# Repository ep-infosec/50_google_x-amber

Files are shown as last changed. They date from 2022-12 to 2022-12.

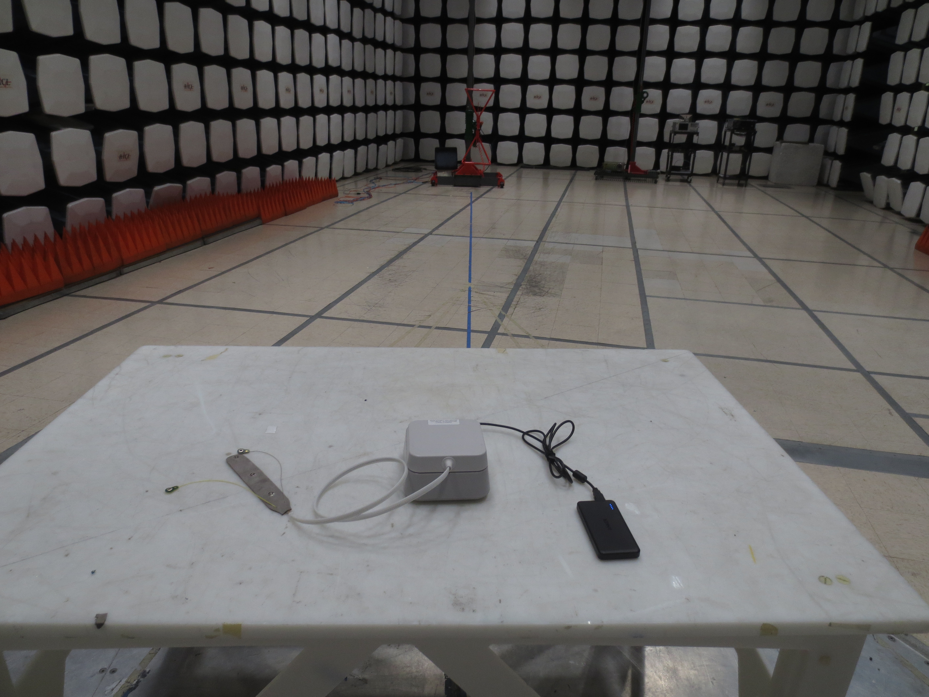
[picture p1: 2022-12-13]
hardware/test/safety reports/IMG_0185.JPG

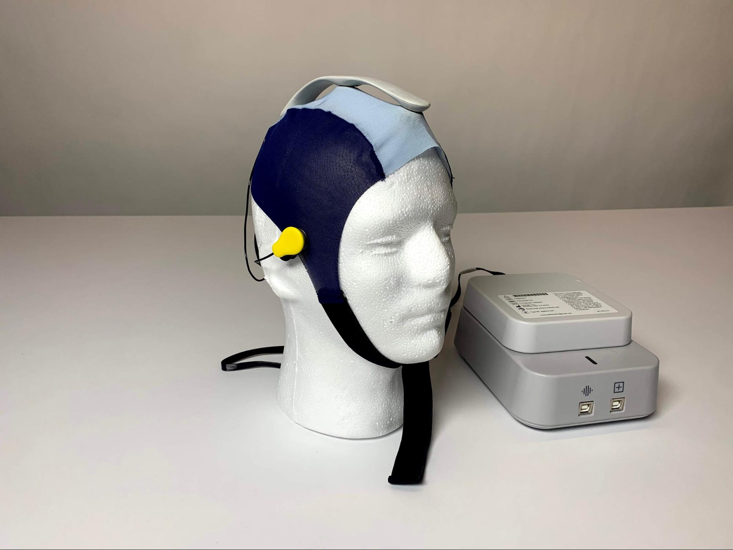
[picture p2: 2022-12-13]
hardware/overview/system_photo.jpg

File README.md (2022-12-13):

# NOTICE
* The materials covered by the associated license relate to a general purpose product and its underlying designs, schematics, and hardware and software code (collectively “Contributions”), none of which have been evaluated, cleared or approved for any medical or other purpose by and may not meet applicable safety or other legal or regulatory requirements of any governmental agency, including but not limited to the United States Food and Drug Administration (“FDA”), or equivalent regulatory bodies outside of the US.
* Any use of the term “EEG” or “electroencephalogram” contained in the Contribution is for informational purposes only and does not label, represent or otherwise indicate the Contribution is intended to be used or has been reviewed or approved as a medical device by the US FDA or equivalent regulatory bodies outside of the US.
* Any article, material or other publication by any person or entity referencing the use or operation of the Contribution for a medical or other any other purpose is for informational purposes only; does not directly or indirectly represent or infer any intended use in the diagnosis of disease or other conditions, or in the cure, mitigation, treatment, or prevention of disease, in people or animals; and does not label, represent or otherwise indicate the Contribution is intended to be used or has been reviewed or approved as a medical device by the US FDA or equivalent regulatory bodies outside of the US.
* While the Contributions may have potential medical applications, many countries, including the US, require regulatory approvals prior to using any device in the diagnosis of disease or other conditions, or in the cure, mitigation, treatment, or prevention of disease, in people or animals.
* It is the user’s responsibility to secure all necessary regulatory approvals and meeting all applicable government safety and environmental standards associated with use of the Contributions.

# Components
This codebase consists of the following components:
* **Software** components below are under Apache 2.0 License:
  1. **Stimulus software** is under `stimulus/` directory.
  2. **Collect software** is under `collect/` directory.
  3. **Firmware** is under `firmware/` directory.
  4. **Flash Tool** is under `flash_tool/` directory.
* **Hardware design** is under CC BY 4.0 License and located in `hardware/` directory.

Please refer to the `README` file and documentations in each respective
directory for more details.

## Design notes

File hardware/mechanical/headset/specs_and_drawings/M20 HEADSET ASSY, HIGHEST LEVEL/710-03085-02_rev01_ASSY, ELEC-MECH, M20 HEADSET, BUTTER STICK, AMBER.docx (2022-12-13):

ITEM ⁴ ³ ² ¹

NUMBER DESCRIPTION MANUFACTURER MFG PART NUMBER QTY.

REVISIONS

1 710-03081-01 ASSY, ELECT-MECH, M20 ADAPTER, BUTTER STICK, AMBER N/A N/A 1

ECO REV. DESCRIPTION BY DATE

2 725-01312-01 ASSY, HARNESS, CABLE, LINEAR SENSORESTRIP N/A N/A 1

ECO-033387 01 INITIAL RELEASE EMT 12/19/2019

3 961-00021-01 LABEL, 5 SENSOR HEADSET, AMBER N/A N/A 1

D

D3 1 2 CCB BCENTER LABEL HORIZONTALLY & FROM APPROXIMATELY BOTTOM EDGE, 11mm AS SHOWN

TEXT ORIENTATION

CONFIDENTIAL THIS DOCUMENT AND THE DATA DISCLOSED HEREIN OR DRAWN

DATE WHEREWITH IS NOT TO BE REPRODUCED, USED, OR RD/EMT/DSF 1/3/2020 A11 DISCLOSED IN WHOLE OR IN PART TO ANYONE WITHOUT THE PERMISSION OF GOOGLE, INC.

CHECKED

DATE G. LEVINE 1/3/2020

43 SHEET 1 OF 1

100 Mayfield Avenue Mountain View CA 94043 UNLESS OTHERWISE SPECIFIED ENGINEER DIMENSIONS ARE IN MILLIMETERS

USA

A

TOLERANCES UNLESS OTHERWISE NOTED:

1.

FOR ASSEMBLY: REFER TO MPI-0306-00, ASSEMBLY INSTRUCTIONS. X X.X X.XX ANGLES

1.0 0.3 .1 .25

G. LEVINE 1/3/2020

THIRD ANGLE

MATERIAL

N/A

TITLE

ASSY, ELEC-MECH, M20 HEADSET, BUTTER STICK, AMBER

2.

PART REQUIRES PACKAGING TO PREVENT DAMAGE DURING SHIPMENT. PROJECTION

FINISH

1.6

N/A

SIZE BSURFACE ROUGHNESS

UNLESS OTHERWISE SPECIFIED

BREAK SHARP EDGES TO <0.4 MM

DO NOT SCALE DRAWING

1:10 710-03085-02 2 1

PART NUMBER

710-03085-02

REV

01

INTERPRET DRAWING PER ASME Y14.5-2009

SCALE

FILE NAME

MASS (g):

267.64

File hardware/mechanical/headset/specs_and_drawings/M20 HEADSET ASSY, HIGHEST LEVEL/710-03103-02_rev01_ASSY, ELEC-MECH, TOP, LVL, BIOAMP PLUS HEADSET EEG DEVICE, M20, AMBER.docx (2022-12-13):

ITEM ⁴ ³ ² ¹

NUMBER DESCRIPTION MANUFACTURER MFG PART NUMBER QTY.

1 710-03064-01 ASSY, M20 BIOAMP, BUTTER DISH, AMBER N/A N/A 1

2 710-03085-02 ASSY, ELEC-MECH, M20 HEADSET, BUTTER STICK, AMBER N/A N/A 1

D DCC1 2 B BACONFIDENTIAL

THIS DOCUMENT AND THE DATA DISCLOSED HEREIN OR DRAWN RD/EMT/DSF WHEREWITH IS NOT TO BE REPRODUCED, USED, OR DISCLOSED IN WHOLE OR IN PART TO ANYONE WITHOUT THE PERMISSION OF GOOGLE, INC.

CHECKED

G. LEVINE DATE

1/3/2020 DATE

1/3/2020 100 Mayfield Avenue Mountain View CA 94043 UNLESS OTHERWISE SPECIFIED ENGINEER DIMENSIONS ARE IN MILLIMETERS

USA

A

TOLERANCES UNLESS OTHERWISE NOTED:

G. LEVINE 1/3/2020 MATERIAL

TITLE 1. PART REQUIRES PACKAGING TO PREVENT DAMAGE DURING SHIPMENT. 2.

PART PACKAGING REQUIRES LABELING OF PART NUMBER AND MANUFACTURER NAME X X.X X.XX ANGLES

SIZE BDO NOT SCALE DRAWING N/A

710-03103-02 688.65 43 2 1

SHEET 1 OF 1 1.0 0.3 1. .25

THIRD ANGLE

N/A

ASSY, ELEC-MECH, TOP, LVL, BIOAMP PLUS HEADSET EEG DEVICE, M20, AMBER

PROJECTION

FINISH

1.6

N/A

SURFACE ROUGHNESS

UNLESS OTHERWISE SPECIFIED

PART NUMBER 710-03103-02

REV

01

SCALE

FILE NAME

MASS (g):

BREAK SHARP EDGES TO <0.4 MM

INTERPRET DRAWING PER ASME Y14.5-2009

REVISIONS

ECO REV. DESCRIPTION BY DATE

ECO-033387 01 INITIAL RELEASE EMT 12/19/2019

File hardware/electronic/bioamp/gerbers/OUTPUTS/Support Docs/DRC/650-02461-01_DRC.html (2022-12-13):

Altium

# Design Rule Verification Report

Date: | | 5/15/2019
Time: | | 4:19:37 PM
Elapsed Time: | | 00:00:04
Filename: | | G:\My Drive\Amber\6. Hardware\Bio-amplifier Schematics and PCB Files\Luchador Rev 3.2b\Pcb\Luchador Pcb.PcbDoc

Warnings: | | 0
Rule Violations: | | 5

## Summary

Warnings | Count
Total | 0

Rule Violations | Count
Clearance Constraint (Gap=6mil) (All),(All) | 5
Clearance Constraint (Gap=10mil) (InNamedPolygon('PWR GND') Or InNamedPolygon('BOT GND') Or InNamedPolygon('SL2 GND') Or InNamedPolygon('SL1 GND') Or InNamedPolygon('TOP GND')),(All) | 0
Clearance Constraint (Gap=10mil) (InNamedPolygon('-2.5V')),(All) | 0
Short-Circuit Constraint (Allowed=No) (All),(All) | 0
Un-Routed Net Constraint ( (All) ) | 0
Modified Polygon (Allow modified: No), (Allow shelved: No) | 0
Width Constraint (Min=6mil) (Max=100mil) (Preferred=10mil) (All) | 0
Power Plane Connect Rule(Direct Connect )(Expansion=20mil) (Conductor Width=10mil) (Air Gap=10mil) (Entries=4) (All) | 0
Hole To Hole Clearance (Gap=10mil) (All),(All) | 0
Net Antennae (Tolerance=0mil) (All) | 0
Height Constraint (Min=0mil) (Max=1000mil) (Prefered=500mil) (All) | 0
Total | 5

Clearance Constraint (Gap=6mil) (All),(All)

Clearance Constraint: (Collision < 6mil) Between Arc (3056mil,4335mil) on Keep-Out Layer And Pad J8-M(3056mil,4335mil) on Multi-Layer

Clearance Constraint: (Collision < 6mil) Between Arc (3056mil,4460mil) on Keep-Out Layer And Pad J8-M(3056mil,4460mil) on Multi-Layer

Clearance Constraint: (201617.964mil < 6mil) Between Arc (3156mil,4335mil) on Keep-Out Layer And Pad J8-M(3156mil,4335mil) on Multi-Layer

Clearance Constraint: (Collision < 6mil) Between Arc (3256mil,4335mil) on Keep-Out Layer And Pad J8-M(3256mil,4335mil) on Multi-Layer

Clearance Constraint: (Collision < 6mil) Between Arc (3256mil,4460mil) on Keep-Out Layer And Pad J8-M(3256mil,4460mil) on Multi-Layer

Back to top

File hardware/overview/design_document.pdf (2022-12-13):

# Draft: 2019-08 AMBER M20 EEG Acquisition System Design Document

### 1. The M20 Bioamplifier

M20 is a 32 channel EEG acquisition system. It is designed to be connected to a PC USB port for data communication.

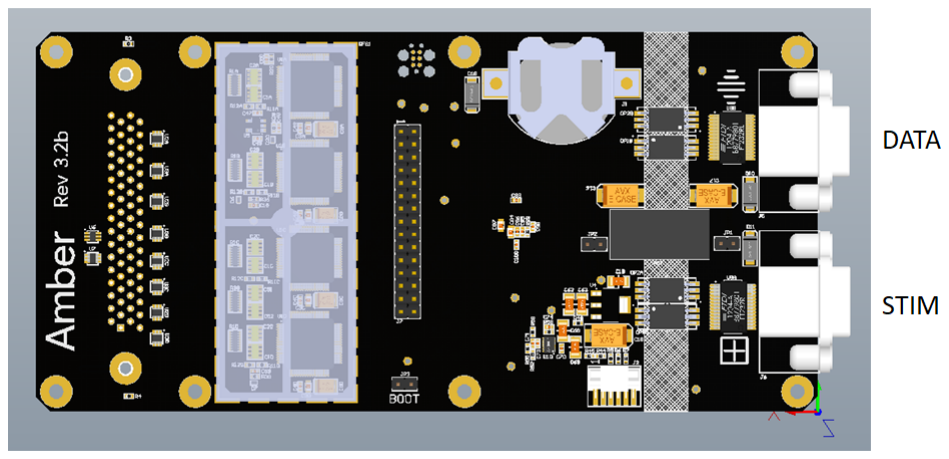
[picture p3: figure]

### 1. Hardware Design

### 1.1. DAQ

The heart of the design is the ADS1299 8 channel bioamplifier from Texas Instruments. This single IC provides the front-end amplification and 24 bit conversion. It is particularly suitable for EEG measurements as it provides a ground bias generator and built-in lead-off detection.

4 of the ADS1299s are connected together in a parallel data configuration. All 4 together provide 32 EEG channels. U1A is the master ADS1299 and provides the conversion clock to the other 3 converters to keep things synchronized. U1A is also the master bias generator.

Although the ADS1299 can provide differential or single-ended inputs, the configuration of the board allows for only single-ended inputs on channels 1-24, and the option of single-ended or differential inputs on channels 25-32.

The sample rate is 250 samples per second.

Communication with the MCU is over 4 wire SPI running at a clock speed of 4 MHz. The ADS1299 provides a signal (#DRDY) that goes low when a conversion is ready to be read out of the chip. Only the master has this signal connected to the MCU and as all timing is referenced to it. Individual chip selects are asserted to read the data from each of the ADS1299s in turn. An alternate option would be to read the data in a daisy-chain configuration, but the parallel configuration was chosen for its speed and flexibility.

### 1.2. MCU

The MCU is a Kinetis (NXP/Freescale) KL27Z256 in a 64 pin QFP package. This is an Arm Cortex M0 processor running at 48 MHz with 256K of flash memory. The reasons for choosing this processor include the speed, cost, availability, and ease of development with the Kinetis tool chain.

Debugging is done through a dedicated JTAG port implemented with a special TAG connect cable. Production programming is done through the DATA USB port utilizing the built-in ROM bootloader and a special Python tool.

The MCU handles the data conversion from the ADS1299s and communication with the host PC. It is also responsible for monitoring the on-board power supplies.

4 input pins allow for identifying the hardware revision through pull-down resistors. 4 pins are also reserved for future expansion.

Although the MCU has low-power modes, in this design it is always running at full power.

### 1.3. Power Supplies

Power to the board comes from either one of the 2 USB connectors. USB voltage is diode-ORed and powers an isolated DC/DC converter (PS1). This provides the 4kv isolation and patient leakage current protection. Jumpers JP1 and JP2 must be installed for normal operation. These were implemented to provide power flexibility in the event a battery would need to be used.

The 5V output of the DC/DC converter is linear regulated down to 3.3V. A linear regulated was chosen to provide a lower noise floor than another DC/DC. The 3.3V primary powers the MCU and digital logic.

A charge pump based converter also runs off the 3.3V rail and provides the +/-2.5V rails to the ADS1299s. Normally charge pumps are rather noisy, but this particular IC (LM27762) has built-in linear regulators following the charge pumps and is tailored to these sorts of applications.

A separate 2.5V reference is also generated to power the MCU analog section and to provide a precise reference for power supply measurements.

### 1.4. USB Ports

Two USB ports connect the PCB to a PC. The DATA port is used to transfer the streaming EEG data. The STIM port allows control of the board and is used to set marks in the EEG data stream.

Each port uses an FTDI232 USB to serial IC on the PC side. The MCU side implements optical isolators for patient protection. These are rated at 4kv with a maximum data rate of 10Mbps.

### 1.5. Real Time Clock

A real time clock is implemented. It communicates over I2C with the MCU and has battery backup.

### 1.6. Micro SD

A micro SD slot is provided for future expansion. It is connected to a second SPI port on the MCU.

### 1.7. Expansion/Debug Header

Board test and expansion signals are brought to this header. They are labeled in the layout and provide an easy means of testing or debugging the board.

### 2. Layout

The PCB is designed as a 6 layer board. The layer stack is signal, ground plane, signal, signal, power connections, signal. Minimum line/space is 6/6 and minimum via size is 6/16. Board material is plain FR4 and finish is ENIG. This is standard for today’s fabrication processes and allows the board to be manufactured at any number of board houses.

The board is separated into 3 distinct sections: PC non-isolated, digital, and analog.

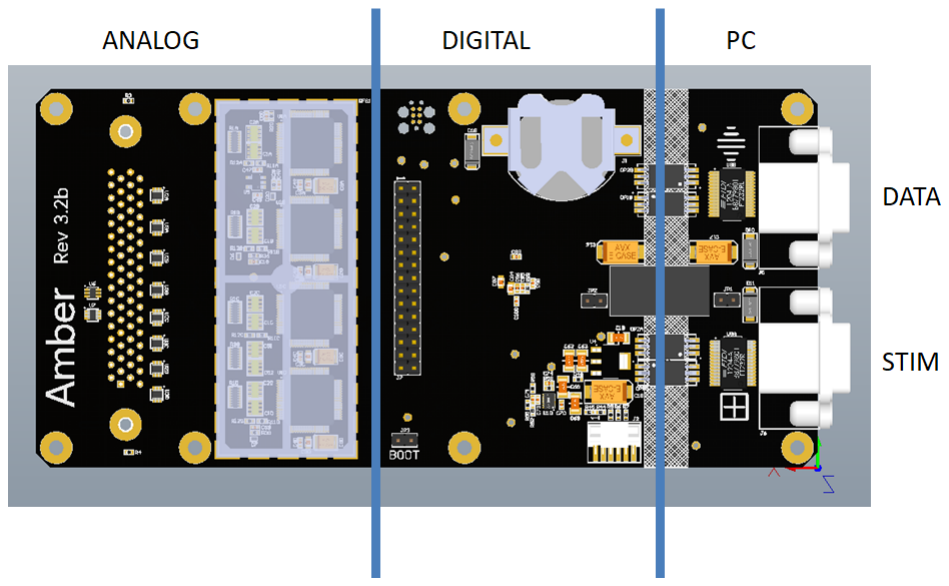
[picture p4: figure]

### 2.1. PC

The PC side has the USB ports and half the optical isolators and DC/DC converter. Creepage and clearance is maintained at 8mm.

### 2.2. Digital

The digital section incorporates the power supplies and MCU. The expansion header is also included here.

### 2.3. Analog

The analog section protects the microvolt level EEG signals from the noisy digital sections. An RF shield is included that encapsulates the ADS1299 converters. A split ground plane separates the sensitive ground returns from the noisy digital grounds:

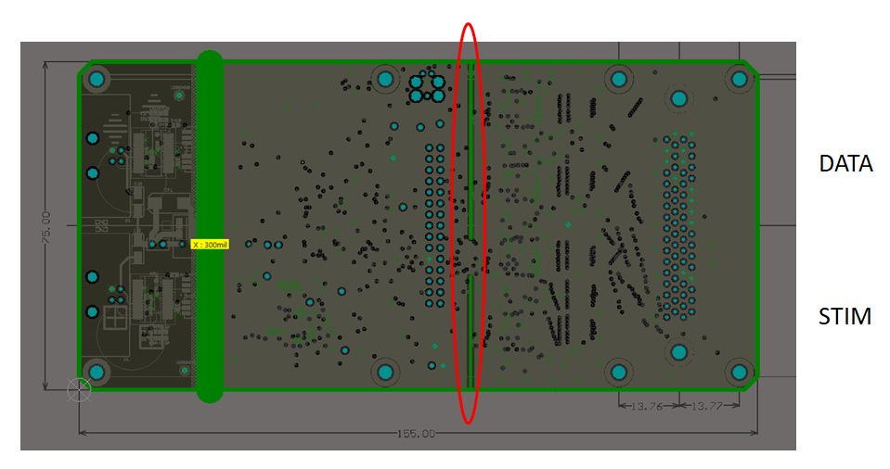
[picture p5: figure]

### 2.4. Test Points

Various individual test points are provided as well as the debug header for future automated testing.

### 3. Firmware

The firmware was developed in C using the Kinetis Design Studio. Some functions were developed with the help of Kinetis’s Processor Expert which simplifies MCU configuration parameters. Some low-level drivers were hand written for the high performance and low latency needed processing the EEG data.

A main loop handles gathering EEG data, doing serial communication, and blinking LEDs. Some tasks are event driven such as EEG data ready and serial communication. These typically either buffer the data or raise flags for processing in the main loop.

A text based command line interpreter (CLI) is implemented for easy control and communication. Any terminal program can be used for sending commands. Although the CLI will respond to commands from either port, only characters on the STIM port are echoed. CLI responses on the DATA port are multiplexed with the streaming EEG data by prefixing ‘CLI:’ to the response line. Commands to the CLI are terminated by a carriage return.

EEG data is continuously streamed on the DATA port in ASCII format. Each channel is comma separated and the EEG value is encoded as a signed 24 bit value. A frame of EEG data has the following format:

SEQUENCE NUMBER | CH 1 | CH 2 | … | CH32 | MARK | CR/LF

The frame is prefixed by ‘DATA:’. The sequence number is an auto incrementing unsigned 32 bit value. The mark is a user-selected data value appended to the EEG stream. Each line is terminated by a carriage return/line feed.

M20 Active Sensor Breakout Board Design Document

## 1. Overview

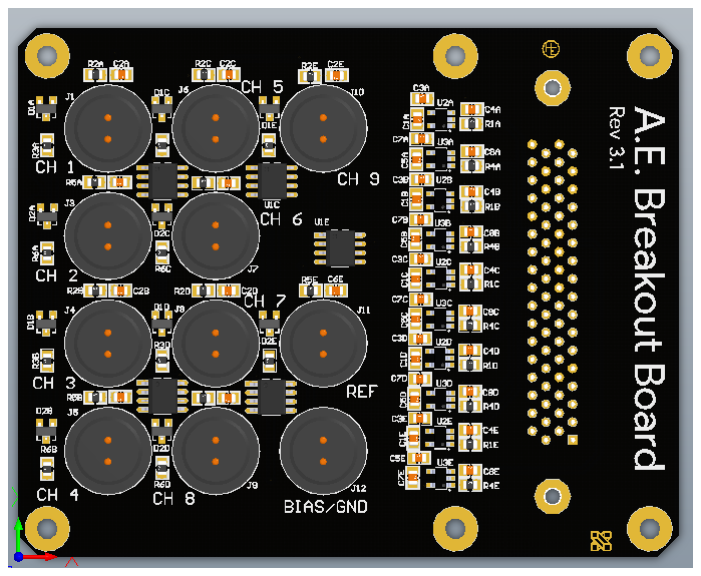
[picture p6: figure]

Conventional wet EEG sensors rely on electrolytic gels to penetrate hair and provide a clean conductive path between sensor and skin. The gel also 'fills-in' potential gaps formed between the sensor and skin during application and subject movement. The use of wet EEG sensors is time consuming and uncomfortable for the subject.

The M20 bioamplifier program remedies this by using dry electrodes. Dry electrodes have a higher impedance than wet electrodes. M20’s dry electrode solution combines sensors with mechanics and electronics which match the higher impedance. These are known as active sensors. A high impedance preamplifier circuit is integrated with the dry sensor to provide the bioamp with a clean signal. Typical active sensors require three wires, 2 for power and 1 for the signal. M20’s active sensors are powered by a current source requiring only 2 wires running to the electrode. The circuitry for the current source is integrated into the active electrodes adapter board that plugs into the bioamp.

The Active Electrode Breakout Board is used with the AMBER EEG Bioamplifer to make electrical connections with the test subject. It includes 9 channels of EEG plus reference and bias connections.

## 2. Design

## 2.1. Electrical

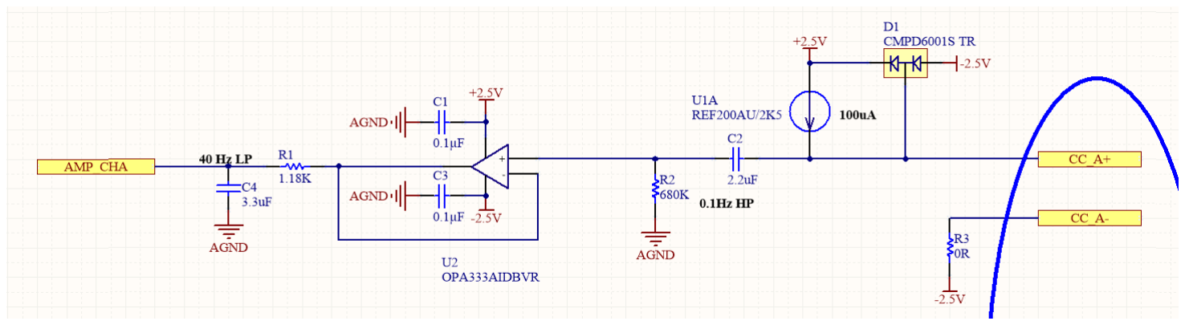
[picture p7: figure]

The electrical design of each EEG channels includes a 100uA current source. This powers the electrode, which is an operation-amplifier operating in a bootstrap mode. Microvolt signals from the operational amplifier electrode are high-pass filtered at 0.1Hz and buffered, then low-pass filtered at 40 Hz. This filtered and buffered signal is presented to the bioamplifier board.

The reference electrode is similarly processed as an EEG electrode.

The bias electrode is simply passed through without any electrical processing.

## 2.2. Mechanical

## 2.2.1. Electrodes

The electrodes connect to the breakout board through an industry-standard touchless connector from Plastics1. The touchless connector ensures that no electrical conductor can be accidently touched during the operation of the EEG system.

## 2.2.2. Main Connector

The connection to the AMBER bioamplifier is made through a 68 pin vertical SCSCI connector.

## 2.2.3. PCB

The PCB is a 4 layer standard FR-4 substrate. The size is 94x75mm.

Firmware Design

## 1. Overview

The firmware for the Amber project is responsible for taking EEG samples from the ADS1299 and formatting them for serial delivery to an external PC. It will also accept commands from a second serial port that is running a basic CLI (Command Line Interpreter). It is designed to run on an NXP MKL27Z256VLH4 processor.

## 2. Structure

All of the code runs in a single thread; therefore, each task must maintain its own state machine and relinquish orderly control to prevent the system from blocking. Each task is called from the main loop in the main.c module. The tasks are as follows:

1. Leds
2. EEG
3. Serial

## 2.1. Processor Expert

Processor Expert is an automatic code and configuration generator by NXP. It is used to speed up development of firmware for specific microcontrollers by abstracting to driver-level code. It is used extensively in this project. The modules will be described later in this document.

## 3. Modules

## 3.1. main.c

The entry point into the firmware is main.c. However, before the first line in main.c has been executed, C initialization routines have already been run to initialize static data structures. This occurs in the background and is invisible to the developer.

The first task is to initialize the Processor Expert(PE) modules. This includes setting the CPU clock and operating modes.

Following the PE initialization, the firmware initializes serial communication, LEDs, SPI communication (used with the ADS1299 converters), and EEG data structures. After initialization is complete, the main loop starts to service the LED, EEG, and serial tasks.

## 3.2. eeg.c

This module is responsible for high-level communication with the ADS1299. It includes functions for initializing the converters and reading and writing the ADS1299 registers. The EEG task checks if there is data to be read from the converters and calls the function to read that data.

## 3.3. spi.c

This module contains the low-level functions to communicate with the ADS1299 converters. It is responsible for setting the chip-select pins and performing low-level reads and writes of the converter registers and also the EEG data.

EEG data is read from each of the four ADS1299 converters in turn. Starting from converter 0, EEG data is clocked in from each of the 8 channels per converter, including a status register. Each channel’s 24 bit EEG data is placed into a 32 bit data structure and pushed onto a queue. This queue is used by the serial task to transmit the data to the host PC. The queue should never be completely filled in normal operating conditions. In the case that the queue fills up, data will be overwritten.

Registers in the ADS1299 that need to be updated are written immediately after EEG is read to prevent timing issues and data loss.

## 3.4. leds.c

This module contains functions for setting the various board LEDs. The LED task is responsible for blinking the green status LED.

## 3.5. serial.c

This module contains the serial task and low-level functions to send data to the serial ports. Buffering and actually transmitting the data is handled by the UART PE module.

The serial task checks for new EEG data and packages it into a data string. This is transmitted by the PE module to the PC.

It also checks for new characters received on the data or mark serial ports. This is passed to the CLI and the response is sent to the serial port.

## 3.6. cli.c

This module handles the command interpreters on both the data and mark ports.

It takes serial input from the serial module and cleans and parses it. The sentence is parsed into a command string, and an argument string. The command string is fed into a large if-else-if structure to compare it to known commands and the arguments are evaluated. An output string is passed back to the serial module for transmission to the host.

## 3.7. Events.c

This module handles so-called events from the PE code. These are really post-processed interrupts from each PE module.

Significant interrupts are the UART interrupts and timer interrupt. The UART interrupts are called whenever a character is received from the host PC. This is transferred to the serial module and placed into a buffer to be parsed by the CLI.

The timer interrupt is triggered every millisecond and decrements various timer variables used by the modules.

## 3.8. version.c

This module reports the version and serial number of the firmware.

## 3.9. settings.h

This header file includes project-wide settings.

## 4. Processor Expert Modules

The following modules are part of the Processor Expert build system. These modules are compiled from PE GUI settings and provide driver-level access to the hardware.

## 4.1. CPU

This module allows low-level access to the CPU hardware. Oscillator, memory, and operating mode settings are provided by this module. This is where the master core clock is set to 48MHz.

## 4.2. Serial_LDD

This low-level driver module provides access to the serial UART. Two instances are instantiated for UART0 and UART1. Baud rate and other communication settings are configured with this module. The methods exposed include ‘SendBlock’ for sending data, and ‘ReceiveBlock’ for receiving data. Events include the data received interrupt.

## 4.3. TimerInt_LDD

This module configures the timer interrupt. This timer can be used for an embedded RTOS, but in this instance it generates an interrupt every millisecond to decrement timer variables used by various functions in the system.

The timer is auto-initialized and generates the timer interrupt event.

## 4.4. SPIMaster_LDD

This module interfaces with the SPI hardware on the microcontroller. Using this module, SPI pins, clock frequency, and phase are configured. Data to the ADS1299 converters are sent using this module.

This module provides the ‘SendBlock’ and ‘ReceiveBlock’ methods; however, these built-in functions are not used because they require a large latency which is unacceptable. The actual SPI subsystem is accessed through the registers for the lowest latency transmissions.

## 4.5. BitIO_LDD

Multiple instances of this module handle the GPIO operations of the MCU. This module allows the firmware to setup GPIO pin, direction, speed, and drive strength. This module is used to drive all the chip-select pins for ADS1299 access and LEDs.

## 4.6. Flash_LDD

This module handles FLASH memory reads and writes. This is primarily used to store the serial number of the device.

## 5. Building firmware

To build the firmware, Kinetis Design Studio 3.2 is used, although gcc should work for a complete project. KDS is required to work with the PE tools and modules. Also, KSDK1.3 will need to be downloaded and installed.

Install KDS 3.2, then select File-Import-Existing Projects into Workspace. Select the project directory and all files will be loaded into the workspace. Building is as simple as selecting ‘build’.

## 6. Flashing

Flashing a board can either be accomplished with a JTAG debugger and KDS, or via USB and the compiled BIN file. For instructions, see the flash document.

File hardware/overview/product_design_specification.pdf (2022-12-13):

EEG Product Design Specification | xxx-xxxxx-00 Rev 1

# 1. Introduction

## 1.1. Purpose

# 2. Overview

## 2.1. System Overview

The M20 EEG Device (Component 1 see Fig. 1) has 4 primary components:

1) Headset, which consists of an adapter and sensor strip pair,
2) Headset accessories: textile caps, sensors, and ear clips/stickers,
3) Bioamplifier (bioamp),
4) Collect Software [Visualization software]. Note: Collect runs on a Windows laptop referred to as the Visualization laptop

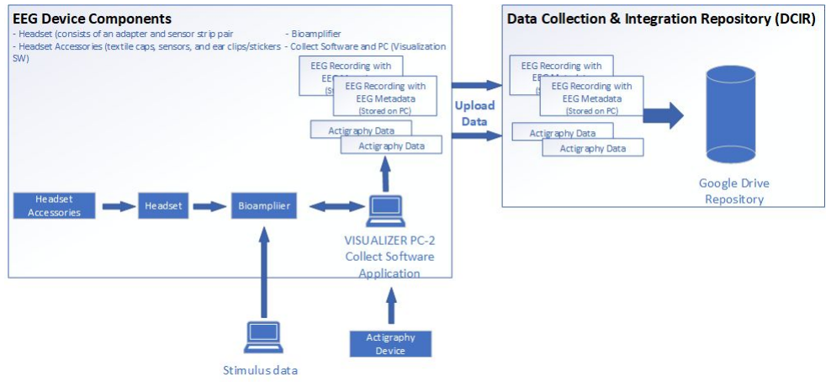
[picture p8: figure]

Figure 1: End-to-end M20 System Diagram for use in Clinical Investigation

For Internal Use Only. This document contains confidential, proprietary information. It may not be copied or reproduced without permission.

Rev 1

# 3. References

## 3.1. Applicable Standards

This document demonstrates compliance to the requirements of the following Standards and Regulations:

Document Number | Title
IEC 60086-4 | Battery Standards (Lithium Battery)
IEC 60950-1 | Power Supply
UL 796 | Standard for Printed-Wiring Boards

## 3.2. Internal Documents

The following documents form part of this document. In the event of conflict, this document supersedes:

Document
Number | Title

## 3.3. Abbreviations

Acronym/Term | Definition
EEG | Electroencephalography
Task | Individual stimulus test
Session | One or more contiguous Tasks for a single participant

For Internal Use Only. This document contains confidential, proprietary information.

Rev 1

# 4. Architecture

## 4.1. Hardware Architecture

4.1.1. Bioamplifier to / from Adapter (Headset Unit) w/ Sensor Strip

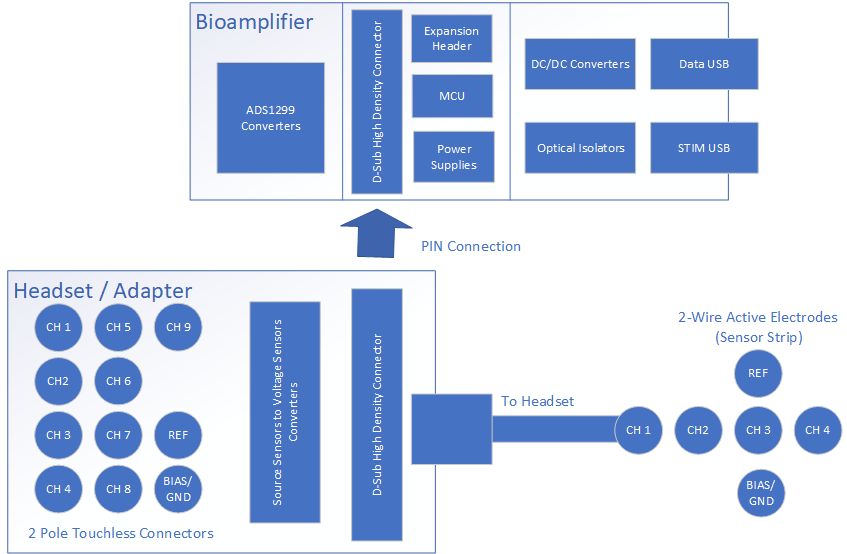
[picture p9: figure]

4.1.1.1. The Headset Adaptor allows connection of sensors that can be converted the sensor source to the voltage source. The sensors are 2-wire active electrodes that connect to the Adapter via 2-pole touchless connectors. These readings can then be transferred through the connector to the Bioamplifier. The Adaptor includes 9 channels of EEG plus reference and bias connections.

For Internal Use Only. This document contains confidential, proprietary information.

Rev 1

4.1.2. Bioamplifier to / from Visualizer PC (w/ collect software system)

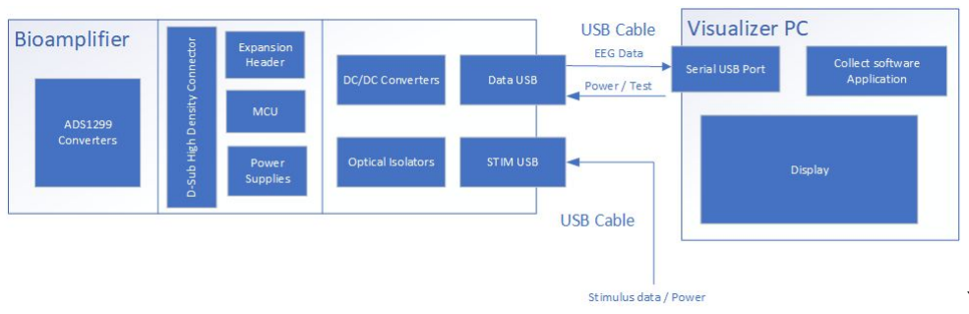
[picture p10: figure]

`
4.1.2.1. The (4) ADS1299 8 channel bioamplifier and processes received sensor data from the Adapter and passes on to the MCU. The MCU is connected to the ADS1299’s and handles the data conversion from the bioamplifiers, communication with the host PC, and monitoring onboard power supplies as well as consolidates EEG data with recieved ‘Mark’ data from the STIM source. 2 USB serve as sources for Bioamplifier power. The STIM USB port allows receiving of Stimulus relevant Mark data at the Bioamplifier. The DATA USB port allows receiving of test initiation and execution data from the Visualizer and sends EEG data received to the Visualizer. Input power from 1 of the 2 USB Ports (STIM and DATA) are regulated ‘down’ by the DC/DC converters. Data sent to the Visualizer is then visualized by the Collect software application continuously.

For Internal Use Only. This document contains confidential, proprietary information.

Rev 1

## 4.2. Software Architecture

4.2.1. Collect Software System

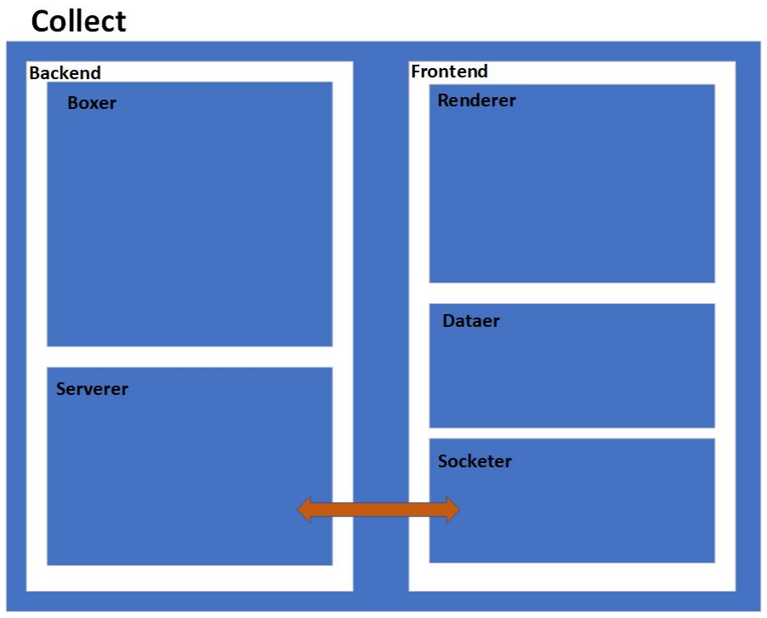
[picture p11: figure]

4.2.1.1. The Collect Software application controls and configures bioamplifier, reads EEG samples from bioamplifier, visualizes EEG data in time and frequency domains for human interpretation
4.2.1.1.1. Records EEG data and metadata to file
4.2.1.1.2. Accepts user input to configure bioamplifier
4.2.1.2. Application Framework
4.2.1.2.1. Application with Node.js backend and Javascript/HTML frontend.
4.2.1.2.2. Backend:
4.2.1.2.2.1. Boxer
communicates with bioamplifier over serial port writes EEG recording to file.
4.2.1.2.2.2. Serverer
Manages IPC (Interprocess Communication) with the Frontend.
4.2.1.2.3. Frontend:

For Internal Use Only. This document contains confidential, proprietary information.

Rev 1

4.2.1.2.3.1. Renders UI for EEG metadata input from user, enable recording, change bioamplifier settings
4.2.1.2.3.2. Renderer
Draws EEG data in time domain or frequency domain.
4.2.1.2.3.3. Dataer
Receives EEG data from backend and processes data for drawing.
4.2.1.2.3.4. Socketer
Manages IPC (Interprocess Communication) with the Backend.
4.2.2. Bioamplifier Firmware

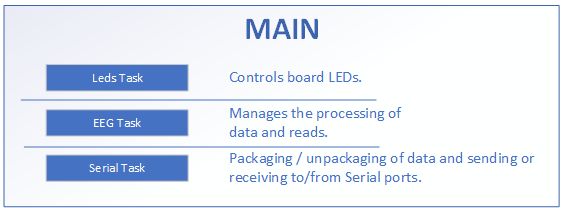
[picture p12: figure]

4.2.2.1. Firmware reads EEG samples from the ADS1299’s and formats for sending to Visualizer System laptop. Single threaded with each task maintaining a separate state machine.Additionally, the firmware accepts Command Line Interpreter (CLI) commands.
4.2.2.2. Firmware utilizes the following primary modules.
- MAIN
- EEG
- SPI
- LEDS
- SERIAL
- CLI
- EVENTS
- VERSION
- SETTINGS
- Processor Expert Modules (Processor Expert build System) - hardware access

For Internal Use Only. This document contains confidential, proprietary information.

Rev 1

# 5. System Design

## 5.1. Collect Software System

5.1.1. User Interface Design
5.1.1.1. Preset channel display options (dropdown selection) Configuration selection for channels used for captured EEG data
- M20 (3 ch) - (default) - display of Fz / Cz / Pz channels
- M20 (4 ch) - display of Fz / Cz / Pz / Oz channels
- 16 Channels - 1-16 channels
- 24 Channels - 1-24 channels
- 32 Channels - 1-32 channels
- FSU Wave 1 - Right Earlobe, Left Upper eye, Left Lower Eye, Left Horizontal Eye, Right Horizontal Eye, Fz, Cz, Pz
- FSU Wave 2 - A2, Fp1, Olat, Oinf, Fz, Cz, Pz
5.1.1.2. Site (dropdown selection) - Site where EEG study is performed.
- M20 - (Default)
- FSU
- MSU
- SDSU
- UF
- UU
5.1.1.3. Tasks (drops down selection) Stimulus tasks associated with captured EEG data
- Doors (Default)
- Emotional Images
- Eyes Closed
- Flankers
- Hot Button
- SRET
- SSVEP
- Oddball
- Test
5.1.1.4. Participant ID (manual entry or arrow selection) Unique ID for participant to associate captured EEG data Numeric only
No Default
5.1.1.5. Session (manual entry)
Session number for the participant Session number default is ‘1’

For Internal Use Only. This document contains confidential, proprietary information.

Rev 1

Numeric only
5.1.1.6. Port (auto / dropdown selection) Selection of port connected to the Bioamplifier
5.1.1.7. Record command Button Prompts user for saving file and beginning the recording of the collected EEG data. This is synchronized with the execution of Stimulus data execution (sessions) with the participant.
5.1.1.7.1. Save recording to directory prompt
File directory selection prompt for selecting folder location
5.1.1.7.2. Record button changes to Stop button
5.1.1.7.3. Time (HH:MM:SS) of Record execution elapsed
5.1.1.7.4. Display of file name and directory folder for saved CSV file displayed in prompt when selecting Stop.
5.1.1.7.5. Displays Recording in Graph display
5.1.1.8. Configuration Icon
Display the administrative settings configurable by user.
5.1.1.8.1. Software Version
Collect software version
5.1.1.8.2. Firmware Version
Bioamplifier firmware version
5.1.1.8.3. Hardware Version Bioamplifier hardware version
5.1.1.8.4. Filter - Order
5.1.1.8.5. Filter - Low Pass - Hz Filter Low Pass Hz amount (40 default) - numeric with arrow option
5.1.1.8.6. Filter - High Pass - Hz Filter High Pass Hz amount (.1 default) - numeric
5.1.1.8.7. Channels
Default to selected Preset channels associated E.g. M20 (3 Ch)
Fz checked
Cz checked
Pz checked
User has option to enter channel labels and check which ones they wish to include - alpha numeric
5.1.1.8.8. New Preset Name
User has the option to enter a new preset name for the selected / entered channels
5.1.1.8.9. Save As New and Apply Command button

For Internal Use Only. This document contains confidential, proprietary information.

Rev 1

Saves the new preset and adds to the list of Presets available for selection
5.1.1.8.10. Send Test Command button Sends a predetermined test message to the Bioamplifier and displays the results on the wave data graph
5.1.1.9. Display Layout
5.1.1.9.1. Display Graph display icon selections
5.1.1.9.1.1. (x axis) % x (y axis) Frequency (hz)
5.1.1.9.1.2. (x axis) uV x (y axis) Time (seconds)
5.1.1.9.2. Left hand side (x-axis) Channels
5.1.1.9.3. Bottom (y-axis) numeric Time or Frequency depending on selection.
5.1.1.9.4. Displays Not Recording - Default display
5.1.1.10. Filer switch
5.1.1.10.1. Turning on the switch highlights in dark blue and applies the configured filter to the display.
5.1.1.10.1.1. Applies the configured filters
Low Pass Hz
High Pass Hz was going on yeah what’s the plan
5.1.1.10.2. Default is off
5.1.1.11. Auto Baseline w/ Continuous checkbox
5.1.1.11.1. Applies a baseline to the graph for each channel
5.1.1.11.2. Default is on
5.1.1.11.3. Continuous checkbox displays the baseline continuously, if not selected the baseline is redrawn repeatingly.
5.1.1.11.4. Not available for the % x Frequency Hz filter
5.1.1.12. uV Peak to Peak Amplitude
5.1.1.12.1. Increasing or decreasing options for increasing peak to peak amplitude displayed.
5.1.1.12.2. 1000 uV default
5.1.1.12.3. Not available for the % x Frequency Hz filter
5.1.1.13. Waveform data
5.1.1.13.1. Current, continuously received EEG waveform is displayed on the interface from left to right with data display varying depending on configuration and filter settings.
5.1.1.13.2. Mark data received from the stimulus system will be displayed as received (at predetermined intervals that represent stimulus participant actions) along with the associated EEG data.

For Internal Use Only. This document contains confidential, proprietary information.

Rev 1

5.1.1.13.3. Each channel configured will display the appropriately mapped sensor data received aligned with the correct channel icon and/or text with each channel separated into sections on the display.
5.1.1.14. Error Message Display
5.1.1.14.1. Error display if no Participant ID entered.
5.1.1.14.2. Error display for access priviledges denied for saving or accessing waveform data file(s).
5.1.1.14.3. Error displayed on startup if configuration unavailable during startup.
5.1.2. File Management
5.1.2.1. Recorded files are stored in default folder : C:\Users\Public\Documents\Recordings\ or other designated folder(s)
5.1.2.2. Files are stored as CSV files.
5.1.2.3. Files have the naming convention [Site][Task][Participant ID][Session] as selected and/or entered on the user interface.
5.1.3. Data Management / Conversion
5.1.3.1. Invoke test message sent from USB to Bioamplifier. [see Bioamplifier - Firmware Software Design for more information]
5.1.3.1.1. Automated Test message sent from the Visualizer System
- Collect Software application upon initialization (Start Up) of the Visualizer system - Collect Software application.
5.1.3.1.2. Manual Test message manually sent to trigger the Bioamplifier to respond with preconfigured EEG data in order to verify test results are received, the Bioamplifier is functioning properly and the Collect Software application is functioning properly.
5.1.3.2. CSV Output files
5.1.3.2.1. Recording output files [see section 5.2.2]. Recording file has 2 parts:Header and Body
5.1.3.2.2. Header
JSON (JavaScript Object Notation) open-standard format. 1 - Collect recording
Specification for recording file header
2 - Channels
Channel description
2.1 - Gain
ADC gain value
2.2 - Index
For Internal Use Only. This document contains confidential, proprietary information.

Rev 1

0-based column index for this channels data in a row 2.3 - IsOn
Channel enabled
2.4 - label
Channel label
3 - Channel count
Number of channels in each row data
4 - Timestamp index
0-based column index for timestamp data in a row 5 - Mark index
0-based column index for mark data in a row
6 - Unit
Channel data unit (microvolt or ADC)
7 - Sample rate
Channel data sample rate in hz
8 - Collect version ( collect software application version) Collect software version that generated this file 9 - Bioamplifier ID
Identifier for the EEG Bioamplifier hardware used 10 - Bioamplifier Version
EEG Bioamplifier Firmware SW Version
11 - Start record datetime
Date and time when the recording is started 12 - Site
Site that generated the recording
13 - Task
Task name performed during the recording 14 - Participant ID
Participant identifier for the recording
15 - Session
Session number for the recording
5.1.3.2.3. Body
Formatted section separated from Header section using format <CR><LF><CR----><LF>
channelCount: [# of channels]
Channels:
{ gain: [#],
Index: [#],
isOn: [true]/[false],

For Internal Use Only. This document contains confidential, proprietary information.

Rev 1

Label: [string] e.g. “Fz”,
},
{ etc… repeat for each channel….}, {
timestampIndex: [#],
markIndex: [#],
unit: [string],
collectVersion: [#.#.#],
bioampId: [string],
bioampVersion: [string], }
Rows of comma-separated values. Data in raw ADC output
Channel gain
One column of mark data
5.1.3.3. Configuration File presets
5.1.3.3.1. Configuration settings from first time use are stored in default Presets folder.
5.1.3.3.2. Saved Presets stored in executable root directory in [presets] folder (loaded automatically on next use).
5.1.3.3.2.1. Automatically updated via Collect Software application.
5.1.3.3.2.2. [preset name]_preset.json
Channels:
{ gain: [#],
isBiasNOn: [true]/[false], isBiasPOn: [true]/[false], isOn: [true]/[false],
Label: [string] e.g. “Fz”,
},
{ etc… repeat for each channel….},
“Name”: [name of preset] }
* All possible channels listed with IsOn false for those not enabled.
5.1.4. Other
5.1.4.1. Keyboard and touchpad allow utilization of all software functionality.

For Internal Use Only. This document contains confidential, proprietary information.

Rev 1

5.1.4.2. WiFi disabled for utilization of Collect Software.
5.1.4.3. All software installed in root directory of executable.
5.1.5. Performance
5.1.5.1. Files are automatically saved during the selection of the Stop Recording command button option.
5.1.5.2. EEG Data is continuously received from the connected USB port and captured automatically during the ‘Recording’ process.
5.1.5.3. The Send Test Command Button option is available for sending test messages to the Bioamplifier in order to verify connectivity and capture of configured test channel results.

## 5.2. Bioamplifier

Fig 1. Bioamplifier PCB

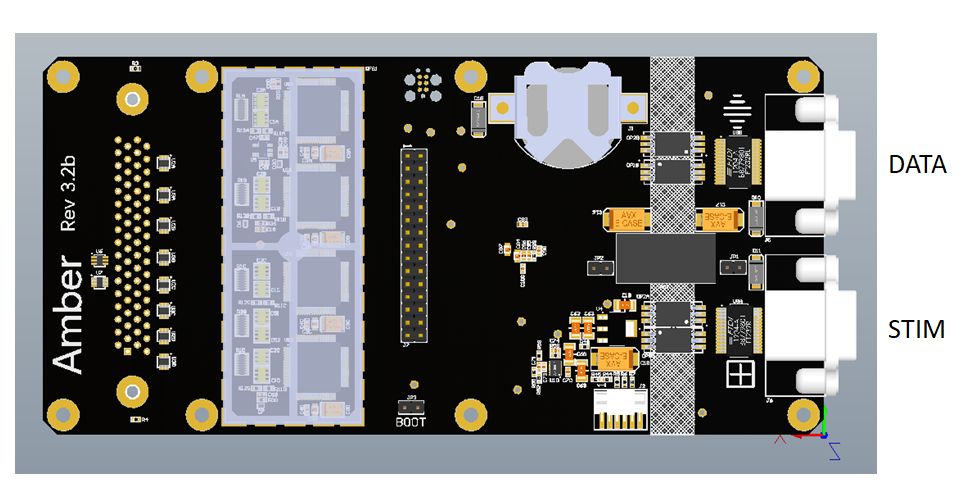
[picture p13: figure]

5.2.1. Firmware Software Design Internal and external drivers utilized for managing firmware response.
5.2.1.1. EEG Data
5.2.1.1.1. EEG Data is continuously streamed on the DATA port in ASCII format.
5.2.1.1.2. Stimulus Mark data is streamed on the STIM port in ASCII format.
5.2.1.1.3. Channels comma separated and encoded as signed 24bit value for each. - handling up to 32 channels of input data.
5.2.1.1.4. Implement command line interpreter (CLI). command to CLI are terminated with carriage return.
5.2.1.1.5. EEG Data collection, Blinking LED’s, and serial communication are managed through a main loop.
5.2.1.1.6. EEG data format:

For Internal Use Only. This document contains confidential, proprietary information.

Rev 1

SEQUENCE
NUMBER | CH 1 | CH 2 | … | CH32 | MARK | CR/LF
5.2.1.1.6.1. EEG Data prefixed by ‘DATA’
5.2.1.1.6.2. Sequence number: Auto incrementing 32bit value
5.2.1.1.6.3. Mark: user -selected data value
5.2.1.1.6.4. CR/LF terminates each line.
5.2.1.1.7. Event Driven or Sent Commands
5.2.1.1.7.1. Echo STIM Port commands
5.2.1.1.7.2. Multiplex DATA Port commands with EEG Data and prefixed with ‘CLI’.
5.2.1.1.7.3. Additional Commands
EEG Data ready
Serial Comm
Power on / off
5.2.1.2. Test Command
5.2.1.2.1. Data message sent from connected Visualizer System -Collect Software Application through serial USB port on Laptop PC, connected USB communication cord, to the DATA USB port on the Bioamplifier.
5.2.1.2.2. Register settings are configured to generate internal amplitude and frequency settings and output to the calling source (the Visualizer System - Collect Software Application)
- Input - Test signal to trigger Bioamplifier response
- Output - Test response with internally generated Amplitude (uV) and Frequency (Hz)
5.2.2. Hardware Design
5.2.2.1. Classification
5.2.2.1.1. FDA Class II Medical Device
5.2.2.2. Overall Layout
5.2.2.2.1. Enclosure - 155mm (W) x 148mm (D) x 57mm (H), 3.3mm thickness
5.2.2.2.2. Unit Weight < 1 kg
5.2.2.3. Operation Mode
5.2.2.3.1. Continuous Operation Mode
5.2.2.4. Temperature Limits
5.2.2.4.1. Operating Temperature 0 to 30℃

For Internal Use Only. This document contains confidential, proprietary information.

Rev 1

5.2.2.4.2. Non-Operating Temperature -20 to 60℃
5.2.2.5. Data Acquisition (DAQ) http://www.ti.com/lit/ds/symlink/ads1299.pdf
5.2.2.5.1. (4) IC ADS1299 - 8 channel bioamplifier (Texas Instruments)
5.2.2.5.2. (1) ADS1299 serves as the master (U1A) and provides the conversion clock to the additional (3) units for synchronizing as well as master bias generator.
5.2.2.5.3. Parallel data configuration (integration).
5.2.2.5.4. Ground bias generator.
5.2.2.5.5. Built in lead-off detection.
5.2.2.5.6. 24 bit conversion
5.2.2.5.7. Channel Inputs
32 Total EEG channels
Single-ended inputs for channels 1-24
Single-ended or differential inputs for channels 25-32
5.2.2.5.8. 250 samples / sec Sample Rate
5.2.2.5.9. MCU communication
4 wire SPI @ clock speed of 4MHz
ADS1299 sends signals that lower for conversion readiness from the chips.
Master IC ADS1299 signal connection with MCU
Chip selects are asserted to read the data from each of the ADS1299s in turn.
5.2.2.5.10. Consolidates Input EEG data with received STIM port data.
5.2.2.6. Microcontroller (MCU)
5.2.2.6.1. 64 pin QFP package Kinetis (NXP/Freescale) KL27Z256
5.2.2.6.2. Arm Cortex M0 processor running at 48 MHz with 256K flash memory.
5.2.2.7. Input Pins
(4) input pins - hardware revision (via pull-down resistors)
(4) pins reserved
5.2.2.8. Power mode
Full-power mode (default)
Low-power mode (optional)
5.2.2.9. Test and Programming Test via dedicated JTAG port implemented via TAG connect cable.
Programming via DATA USB port using built-in bootloader and proprietary tool.

For Internal Use Only. This document contains confidential, proprietary information.

Rev 1

5.2.2.10. Power Supply (Detachable)
5.2.2.10.1. Via (2) USB connectors (either may power board)
5.2.2.10.2. Allow powering from external source for 90 minutes minimum length.
5.2.2.10.3. USB Voltage - diode-ORed
Powers isolated DC to DC Converter (PS1)
4kv isolation and patient leakage current protection
5.2.2.10.4. DC to DC Converter
5V output linear regulated down to 3.3V (low noise floor)
5.2.2.10.5. 3.3V down voltage: Powers MCU and digital logic.
Powers charge pump based converter that provides the +/-2.5v rails to the DAQ ADS1299(s).
5.2.2.10.6. 2.5V reference power Powers MCU Analog section
Provide precise reference for measurements
5.2.2.10.7. Power supply Source Input - 100-240 Vac 50/60 Hz 1.8A (Dell Adapter HAI30PM130)
Output - 19.5Vdc, 7.67A
5.2.2.10.8. Overvoltage Category - OVC II
5.2.2.11. Coin cell battery on PCB
5.2.2.11.1. CR2332 - Lithium Magnesium , 3V, 225mAH, 60℃
5.2.2.12. USB Ports
5.2.2.12.1. (2) USB Ports for PCB Connection to (2) PC’s. Port 1 - DATA Port - Transfer streaming EEG data collected.
Port 2 - STIM Port - Board control and sets marks for the corresponding streaming EEG data collected.
5.2.2.12.2. PC Side - FTDI232 USB to serial IC
5.2.2.12.3. MCU Side - optical isolators for patient protection.
5.2.2.12.4. Rated at 4kv - max data rate 10mbps
5.2.2.12.5. USB Type B, 4 contacts, 1.5A, UL94V-0, Plastic housing, 105℃
5.2.2.13. Real Time Clock
5.2.2.13.1. Communicates over I2C with the MCU
5.2.2.13.2. Battery backup of real time clock.
5.2.2.14. Micro SD
5.2.2.14.1. Connected to a second SPI port on the MCU
5.2.2.15. PCB

For Internal Use Only. This document contains confidential, proprietary information.

Rev 1

5.2.2.15.1. Circuitboard - 155mm x 75mm, 1.6mm thickness, ULV-0, 130℃
5.2.2.15.2. 6 layer PCB board
Layer Stack signal > ground plane > signal > signal > power connections > signal
5.2.2.15.3. Minimum line/space is 6/6 and minimum via size is 6/16.
5.2.2.15.4. Board material is plain FR4 and finish is ENIG.
5.2.2.15.5. Board is separated into (3) sections (PC-non isolated, Digital, Analog)
PC-non isolated - USB Ports, half of the optical isolators, and the DC to DC converters (Creepage and clearance -8mm)
Digital - Power Supplies, MCU and expansion header Analog - Protects the uV EEG Signals from digital noise (split ground plane). An RF shield for encapsulating the ADS1299.

Fig 2 Bioamplifier PCB (with sections)

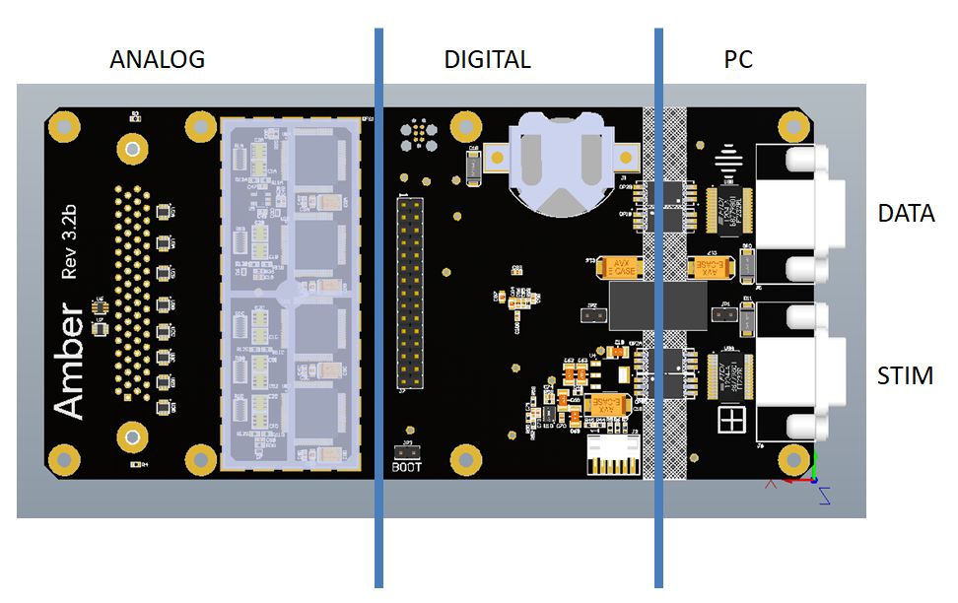
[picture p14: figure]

Fig 3. Bioamplifier PCB (with split ground plane)

For Internal Use Only. This document contains confidential, proprietary information.

Rev 1

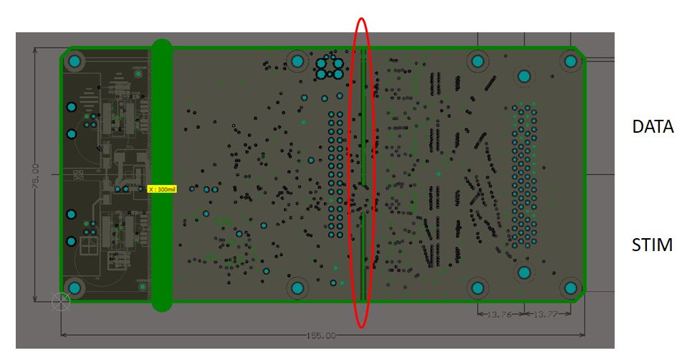
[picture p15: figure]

5.2.2.16. Unit connector
5.2.2.16.1. PCB D-Sub Connector, receptacle type, 68 pos, 1.27mm pitch, 1A max contact current, UL 94V-0, 105℃
5.2.2.16.2. Allows connectivity to Adapter (Headset) attachment -male to female connector setting.
5.2.2.17. Gasket
5.2.2.17.1. O-ring, vulcanized EPDM rubber
5.2.2.17.2. 19mm ring diameter, 1.78mm thickness, 150℃
5.2.2.18. LED’s (Light Emitting Diodes)
5.2.2.18.1. LED for display ‘On’ during powering of device.
5.2.2.18.2. LED for port connection (2) STIM and DATA USB Ports
5.2.2.18.3. LED (4) for activation, programming / test and data communication.
5.2.2.19. Parts Reference
Part Number | Part Type | Description
710-03064-01 | 710-EM Assembly | ASSY, M20 BIOAMP, BUTTER DISH, AMBER
690-13322-01 | 690-Mech Part | MECH, BUTTER AMP TOP, AMBER
690-13321-01 | 690-Mech Part | MECH, BUTTER AMP BOTTOM
690-13335-01 | 690-Mech Part | MECH, LIGHTPIPE, BUTTER
650-02461-01 | 650-PCBA | PCBA, LUCHADOR, REV 3.2b, AMBER

For Internal Use Only. This document contains confidential, proprietary information.

Rev 1

690-13336-01 | 690-Mech Part | MECH, GASKET, LIGHTPIPE, BUTTER, AMBER
690-13337-01 | 690-Mech Part | MECH, BOOT, CONNECTOR, BUTTER
250-06431-00 | 250-Hardware Part | HW, SCREW, THREAD FORMING, TORX RDH, M2.63 x 1.06 THD x 6 MM LG, 18-8 SST, AMBER
250-06430-00 | 250-Hardware Part | HW, SCREW, THREAD FORMING, TORX RDH, M3.63 x 1.34 THD x 10 MM LG, 18-8 SST, AMBER
690-13338-01 | 690-Mech Part | MECH, FOOT, BUTTER
690-13950-01 | 690-Mech Part | MECH, O-RING, 191.26MM ID X 1.78THK, AMBER
690-13430-01 | 690-Mech Part | MECH, GASKET, USB, BUTTER, AMBER
690-13885-01 | 690-Mech Part | MECH, TAPE, VHB RING, AMBER
961-00019-01 | 952-Label | LABEL, INVESTIGATION, REGULATORY, AMBER
5.2.3. Performance
5.2.3.1. MCU must be fast with high availability and simple to develop with product ‘tool chain’.
5.2.3.2. IC (LM27762) - built-in linear regulator to lessen noise output.
5.2.3.3. Proprietary firmware drivers to increase performance and lower latency.
5.2.4. Safety
5.2.4.1. Excessive current and voltage protected by circuit design.
5.2.5. Label
5.2.5.1. Philo M20 Bioamp device shall be labeled per GOO-351-CSD-961-00019-01-DWG .
5.2.5.2. Serial Number format is as follows: BYYMMDD##, where YY are the last two digits of the current year, MM is the current month, DD is the current day, and ## are the number in sequences of devices made on that day (starting with 01).

For Internal Use Only. This document contains confidential, proprietary information.

Rev 1

Fig. 4 Bioamplifier Label

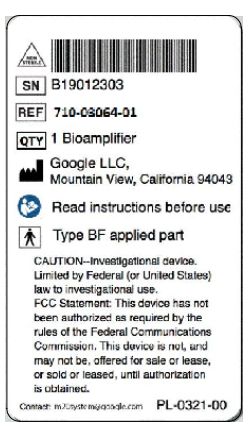
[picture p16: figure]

## 5.3. Adapter (Headset Unit) w/ Sensor Strip

5.3.1. Hardware Design
5.3.1.1. Classification
5.3.1.1.1. FDA Class II Medical Device
5.3.1.2. Overall Layout (Adapter)
5.3.1.2.1. Enclosure - 137mm (L) x 134mm (W) x 49mm (H), 3.3mm thickness
5.3.1.2.2. Unit Weight < 1 kg
5.3.1.3. Operation Mode
5.3.1.3.1. Continuous Operation Mode
5.3.1.4. Temperature Limits
Operating Temperature 0 to 30℃
5.3.1.4.1. Non-Operating Temperature -20 to 60
5.3.1.5. PCB
5.3.1.5.1. Circuitboard - 94mm x 75mm, 1.6mm thickness, ULV-0, 130℃
5.3.1.5.2. 100uA current source for each EEG channel and powers the electrode (operational electrode in bootstrap mode)

For Internal Use Only. This document contains confidential, proprietary information.

Rev 1

5.3.1.5.3. uV signals from operational amplifier are high-pass filtered at .1Hz buffered and low-pass filtered at 40Hz with both signals passed to Bioamplifier.
5.3.1.5.4. Reference electrode processed as EEG electrode.
5.3.1.5.5. Bias electrode is pass-through without processing.
5.3.1.5.6. PCB Board - 4 layer board

Fig. 5 Headset Adaptor PCB

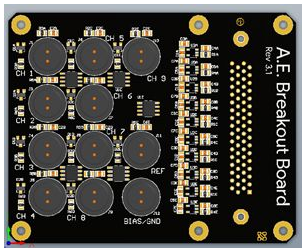
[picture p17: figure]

5.3.1.6. Unit Connector
5.3.1.6.1. PCB D-Sub Connector, plug type, 68 pos, 1.27mm thickness, 1A max contact current, UL 94V-0, 150℃ (SCSCI connector)
5.3.1.6.2. Allows secure connectivity to Bioamplifier unit - male to female connector setting.
5.3.1.7. Sensor Strip - Strip Body
5.3.1.7.1. Synthetic leather - 225mm (L) x 37mm (W), 2.6mm thickness
5.3.1.8. Sensors
5.3.1.8.1. (3) or (4) - 19mm diameter metal base, 1.9mm in diameter 6.6mm high metal, 8 equal distances distributes around base parameter.
5.3.1.8.2. Bias and Reference ear clip attachments.
5.3.1.8.3. Transfer signals collected to the adapter.
5.3.1.8.4. High impedance sensors.
5.3.1.9. Headset - Cap

For Internal Use Only. This document contains confidential, proprietary information.

Rev 1

5.3.1.9.1. The # of sensing electrodes (sensors) are placed in the Fz, Cz, and Pz positions (Oz optional),Two additional electrodes are clipped to the earlobes at A1 and A2.
5.3.1.9.1.1. Caps has holes for attaching 3 sensor or 4 sensor headset attachments.
5.3.1.9.2. Chinstrap attachment
5.3.1.9.3. Flexible material with industry compliant holes positioned for sensors attachment. Flexibility includes ability to apply the Cap with Sensor strip within 3 minutes on participant and will fit a participant with a head diameter of 52-64cm.Verify ability to remove the headset and sensors from the participant in less than 1 minute.
5.3.1.9.4. Durable to envirocide cleaning agent applied up to 9 times to Cap and remain functioning for use. Durability includes ability to use at least 10 times for participant sessions. The sensors and associated wires are protected by the headset.
5.3.1.9.5. The sensors protrude up to 20mm from the headset to allow for hair thickness.
5.3.1.9.6. Headset / Adaptor cable length - 50-250cm.
5.3.1.9.7. The Textile is ‘light weight’ and may be worn under reasonable conditions and allow for signal collection for 60 minutes minimal.
5.3.1.9.8. 2 clip attachments for ear (Bias and Reference sensors)
5.3.1.10. Power Supply
5.3.1.10.1. Allow powering from external source for 90 minutes minimum length.
5.3.1.11. Communication
5.3.1.11.1. EEG Signals collected from Sensors are transmitted to the Adapter.
5.3.1.11.2. Active Sensor Signals from Adapter are then transferred to the Bioamplifier.
5.3.1.12. Cleaning
5.3.1.12.1. Allows wiping down with a soft dry cloth or germicidal disposable wipe.
5.3.1.13. Label
5.3.1.13.1. Philo M20 Headset - Adapter device shall be labeled per PL-0322-00
5.3.1.13.2. Serial Number format is as follows: BYYMMDD##, where YY are the last two digits of the current year, MM is the

For Internal Use Only. This document contains confidential, proprietary information.

Rev 1

current month, DD is the current day, and ## are the number in sequences of devices made on that day (starting with 01).

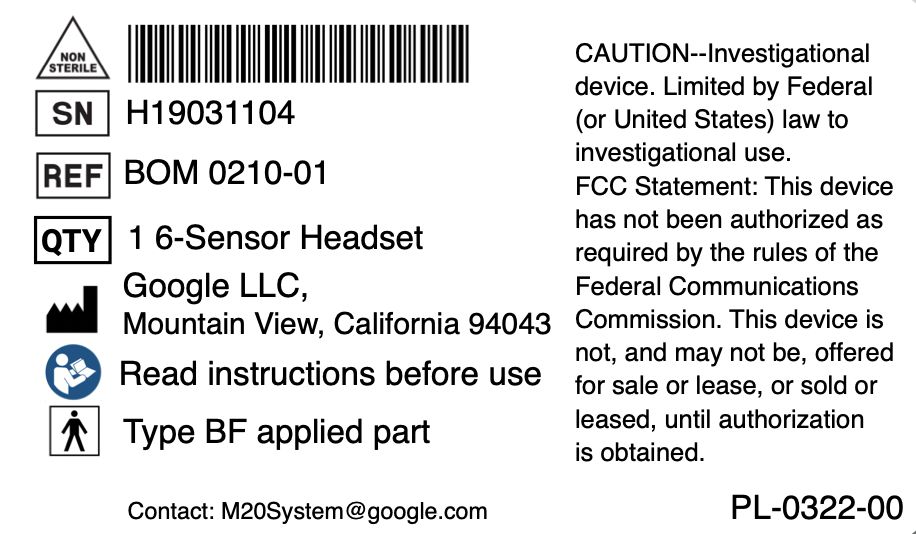
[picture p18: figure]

5.3.1.14. Parts Reference
Part Number | Part Type | Description
690-13313-01 | | MECH BUTTER ADAPTER BOTTOM
690-13320-01 | | MECH BUTTER ADAPTER TOP
250-06431-00 | | HW SCREW, THREAD FORMING,TORX RDH, M2.63 x 1.06 THD x 6 MM LG, 18-8 SST, AMBER
650-02489-01 | | PCBA, A.E BREAKOUT, AMBER
690-13337-01 | | MECH, BOOT, CONNECTOR, BUTTER
250-06430-00 | | HW, SCREW, THREAD FORMING, TORX RDH, M3.63 x 1.34 THD x 10 MM LG, 18-8 SST, AMBER
690-13334-01 | | MECH, GROMMET, BUTTER, AMBER
690-14175-01 | | MECH, O-RING, 149.35MM ID, 1.78 THK, AMBER
710-03081-01 | | ASSY, ELEC-MECH, M20 ADAPTER, BUTTERSTICK, AMBER
725001034-01 | | ASSY, HARNESS, WIRE HARNESS PLUS SENSOR STRI[, M20, AMBER
210-04100-00 | | CONN, CLIP, G.SAHARA, ACTIVE ELECTRODE, AMBER

For Internal Use Only. This document contains confidential, proprietary information.

Rev 1

210-04098-00 | | CONN, REF CLIP, G.ACTIVE ELECTRODE SYSTEM, AMBER
690-14183-01 | | MECH, SENSOR LEATHER STRIP, M20, BOTTOM, GRAY, AMBER
210-04101-00 | | CONN, GROUND CLIP, G.ACTIVE ELECTRODE SYSTEM, AMBER
690-14184-01 | | MECH, SENSOR LEATHER STRIP, M20, TOP, YELLOW, AMBER
250-06645-00 | | HW, TAPE, CLEAR, ADHESIVE DOUBLE SIDED, 3/8IN WD, AMBER
250-06657-00 | | HW, CABLE TIE, 4 IN LG, 10 LB BREAK STRENGTH, NYLON, OFF-WHITE, AMBER
250-06641-00 | | HW, SLEEVING, FLEXO, 3/8 IN, 3/16 IN to 1/2 IN EXP, 500FT, WHT, AMBER
PN-0057-00 | SAHARA clip | SAHARA active electrode clip connector
PN-0058-00 | ACTIVEclipREF | Reference clip connector
PN-0060-00 | ACTIVEclipGND | Ground clip connector
2535-03 | Adhesive Tape | Tanner’s Bond Adhesive Tape
7120K12 | Cable Tie | Narrow, 4" Long, 10 lbs. Breaking Strength, Off-White
PN-0101-00 | Flexo PET | Flexo PET (PTN)

## 5.4. USB Cables

5.4.1. USB 2.0 A (male)/ B(male), 28A WG data wires, 24A WG power wires, 1.8m length.
5.4.1.1. Cable for connectivity from Bioamplifier to Visualizer System.
5.4.1.2. Cable for connectivity from Stimulus System to Bioamplifier.

## 5.5. Laptop Computer

5.5.1. Execution of the Visualizer System (Collect software application)
5.5.1.1. Icon available on the desktop for selection
5.5.1.2. Directory for saving recordings - desktop shortcut
5.5.1.3. 3 Operating System Logins
5.5.1.3.1. Lab Technician

For Internal Use Only. This document contains confidential, proprietary information.

Rev 1

Utilized by site staff for execution of M20 site tests
5.5.1.3.1.1. Limited operating system access
5.5.1.3.1.2. Full access to applications
5.5.1.3.2. Rocket Turtle
Utilized by X-Team staff for managing of M20 site studies.
5.5.1.3.2.1. Increased operating system access
5.5.1.3.2.2. Full access to M20 and most system applications
5.5.1.3.3. Administrative
Restricted to X-Team staff administrators
5.5.1.3.3.1. Full operating system access
5.5.1.3.3.2. Full access to all system application
5.5.1.4. Collect Software application has default user permissions for read / write / delete / execute within directory as well as to output file directory for saved recordings.
5.5.1.5. Collect Software application has full Port Send / Receive access.
5.5.1.6. Collect Software application maximizes application screen resolution to full Laptop screen resolution.
5.5.1.7. System displays the current date and time on the bottom right hand side of the screen. HH:MM AM/PM & MM/DD/YYYY
5.5.2. Software Specification
5.5.2.1. Operating system software - Microsoft Windows 10 Professional 64 bit
5.5.2.2. Collect software application ver. 2.2.3
5.5.2.3. Disk encryption - BitLocker full disk encryption
5.5.2.4. Google Chrome ver. 75+ 64 bit
5.5.2.5. FTDI Driver USB Serial driver supported on Windows 10 Professional
5.5.2.6. DirectX ver 9+
5.5.2.7. Installation Dependencies
5.5.2.7.1. Bower 1.8.8
5.5.2.7.2. Debug 4.1.1
5.5.2.7.3. Electron-Settings 3.2.0
5.5.2.7.4. Express 4.16.2
5.5.2.7.5. Gasp 2.0.2
5.5.2.7.6. Opn 5.4.0
5.5.2.7.7. Serial Port 6.2.1
5.5.2.7.8. Sudo Prompt 8.2.3
5.5.2.7.9. WinReg 1.2.4
5.5.2.7.10. WS 6.0.0
5.5.2.8. Default Presets

For Internal Use Only. This document contains confidential, proprietary information.

Rev 1

5.5.2.8.1. [executable install root directory] > Resources > App > presets
5.5.3. Hardware Specification
5.5.3.1. Processor - i7+, 2.6GHz+ minimum
5.5.3.2. Harddrive - 500GB+ HD
5.5.3.3. Memory - 32GB+ RAM Memory
5.5.3.4. Battery
5.5.3.4.1. 56 WHr+
5.5.3.4.2. 19Vdc input
5.5.3.4.3. Battery will allow 90 minutes+ continuous power without recharge.
5.5.3.5. Keyboard for data entry and selection/navigation.
5.5.3.6. Monitor - 15”+ (1x15x10)
5.5.3.7. Graphics - 59Hz, Intel UHD Graphics 630
5.5.3.8. USB Ports
5.5.3.8.1. Bioamplifier - Serial over USB 2.0 Port
5.5.3.8.2. External Mouse port - USB 2.0 Type A port
5.5.3.9. Default Inactive Lock setting set for 60 minutes. 5.5.3.9

For Internal Use Only. This document contains confidential, proprietary information.

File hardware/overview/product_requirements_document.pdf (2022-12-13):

M20 EEG Device Product Requirements Document (PRD)

990-03834-00
Rev 1
Introduction | 2
Purpose | 2
System Summary Overview | 2
Background | 3
Scope | 3
References | 4
Applicable Standards | 4
Internal Documents | 4
Terminology | 4
Abbreviations | 4
Business Process Overview | 5
Actors/Roles | 5
“To Be” Business Process | 5
Requirements | 7
Regulatory Requirements | 7
Requirements for the Headset and Headset Accessories (M20 3 and M20 4
Configuration) | 7
Requirements for the Bioamplifier | 10
Requirements for the Visualizer System (Collect Software and Installed Computer) 13
Revisions | 18

For Internal Use Only. This document contains confidential, proprietary information. It may not be copied or reproduced without permission.

Document (PRD)

Rev 1

### 1 Introduction

### 1.1 Purpose

This document describes the requirements for the M20 EEG (electroencephalograph) Device, which includes a 3 channel configuration (Fz, Cz, Pz sensor placement) and a 4 channel configuration (Fz, Cz, Pz, Oz sensor placement) (M20 3 & M20 4 respectively). The M20 EEG Device includes the headset, headset accessories, Bioamplifier, and Collect, the visualization software.. See device summary below for details. The requirements include identifying hardware and software, data integration requirements, configuration, and all interfaces with external systems. The general product architecture is described; the requirements for each component of the product are specified. These requirements serve as Design Input for subsequent development activities. Note that the names used in this document are codenames only; actual product names will be determined at a later time.

### 1.2 System Summary Overview

The M20 EEG Device (Component 1 see Fig. 1) has 4 primary components:

1) Headset, which consists of an adapter and sensor strip pair,
2) Headset accessories: textile caps, sensors, and ear clips/stickers,
3) Bioamplifier (bioamp),
4) Collect [visualization software]. Note: Collect runs on a Windows laptop referred to as the Visualization laptop.

The M20 EEG Device (herein referred to as the “Product”) is intended for the acquisition, display, and storage of electrical activity of the brain and optional auxiliary signals through the attachment of two or more sensors at various locations on the body to aid in monitoring and diagnosis.

The Product is intended to be used as one component in the end-to-end data collection system for use in clinical investigations.

For Internal Use Only. This document contains confidential, proprietary information.

Document (PRD)

Rev 1

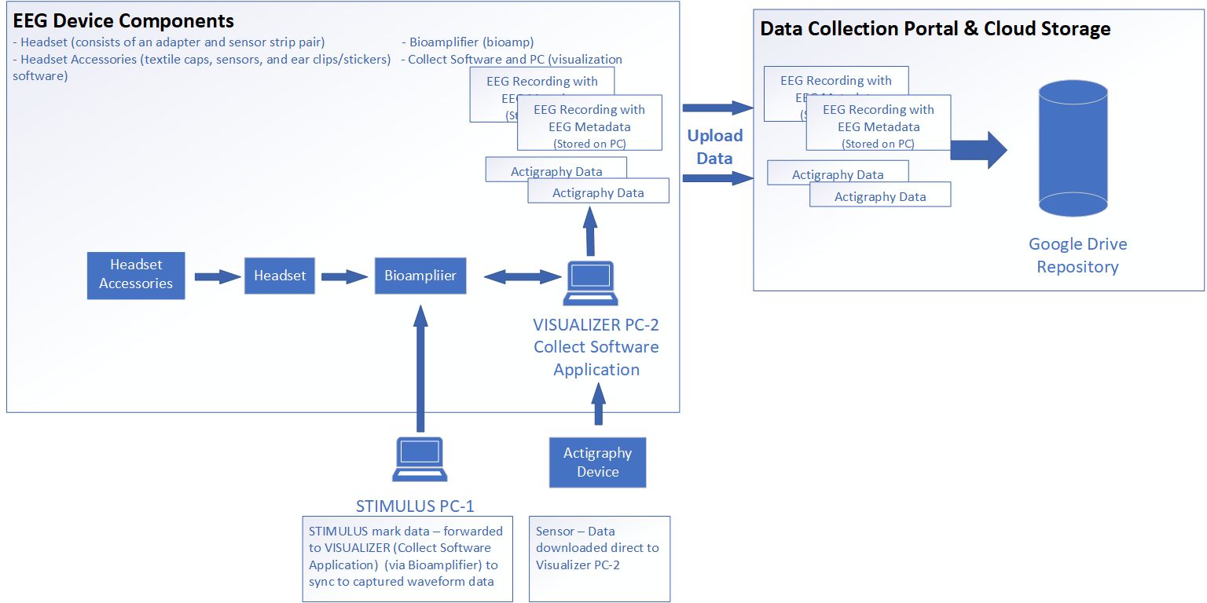
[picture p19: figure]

Figure 1: End-to-end M20 System Diagram for use in Clinical Investigation

### 2 Background

Since EEG caps and devices are not traditionally used by psychologists, psychiatrists, therapists or primary care physicians, user research conducted by X is underway to understand adoption barriers. In order to be easily adopted by and integrated into the standard clinical workflow, we intend to create a convenient, low-maintenance solution at a low cost.

### 3 Scope

This document shall include:

- Business Process overview
- Regulatory Requirements
- Requirements for the Headset, which consists of an adapter and sensor strip pair,
- Requirements for Headset accessories: textile caps, sensors, and ear clips/stickers,
- Requirements for the Bioamplifier (Bioamp)
- Requirements for Collect and the Visualizer laptop

For Internal Use Only. This document contains confidential, proprietary information.

Document (PRD)

Rev 1

### 4 References

### 4.1 Applicable Standards

This document demonstrates compliance to the requirements of the following Standards and Regulations:

Document Number | Title
21 CFR Part 812 | Investigational Device Exemptions
21 CFR Part 820 | Quality System Regulation
IEC 60601-1: 2012 | Medical electrical equipment - Part 1: General requirements for basic safety and essential performance
IEC 60601-1-2 Edition 4.0 2014-02 | Medical electrical equipment - Part 1-2: General requirements for basic safety and essential performance - Collateral Standard: Electromagnetic disturbances -Requirements and tests
n/a | International 10-20 system
IEC-60601-2-26:2012 | Medical electrical equipment - Part 2-26: Particular requirements for the basic safety and essential performance of electroencephalographs

### 4.2 Internal Documents

The following documents form part of this document. In the event of conflict, this document supersedes:

Document Number | Title
990-03806-00 | Design Control
990-03807-00 | Risk Management
990-03813-00 | Software Development Life Cycle

### 5 Terminology

### 5.1 Abbreviations

Acronym/Term | Definition
EEG | Electroencephalography

For Internal Use Only. This document contains confidential, proprietary information.

Document (PRD)

Rev 1

Task | Individual stimulus test
Session | One or more contiguous Tasks for a single participant

### 6 Business Process Overview

### 6.1.1 Actors/Roles

Actor | Role
Study staff | Principal Investigator (PI), Research Assistant, Technician who is responsible for initiating and managing the EEG session.
Administrator (Sponsor staff) | Responsible for configuring, testing, and setup of the EEG system.
Participant | Participates in the EEG session.

6.2 “To Be” Business Process

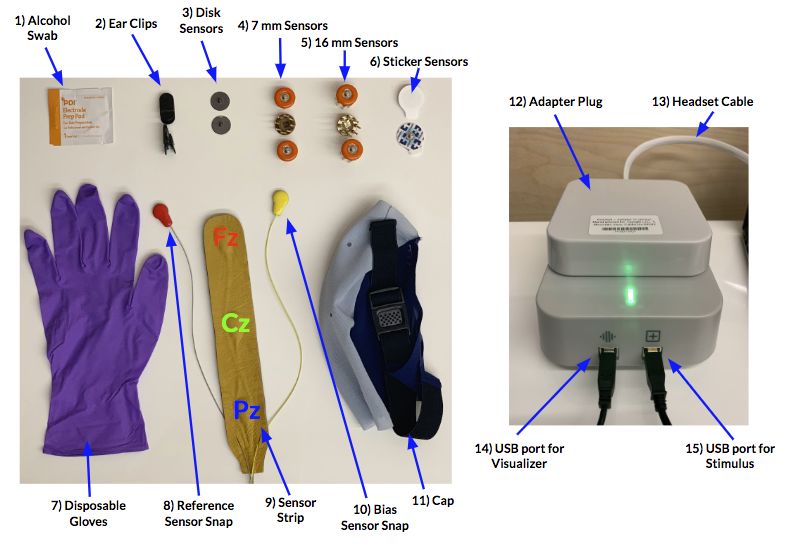
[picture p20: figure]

For Internal Use Only. This document contains confidential, proprietary information.

Document (PRD)

Rev 1

Figure 2: Example design of Product for use in Clinical Investigations.

Setup (daily)
1) Study staff attaches the adapter to the bioamplifier, and the textile cap to the sensor strip as per the IFU.
2) Study staff connects the bioamplifier to the Visualizer and Stimulus laptops.
3) Study staff powers up the devices including the laptops and logs into the Operating System.
4) Study staff launches the Collect and Stimulus software applications to initiate the system.

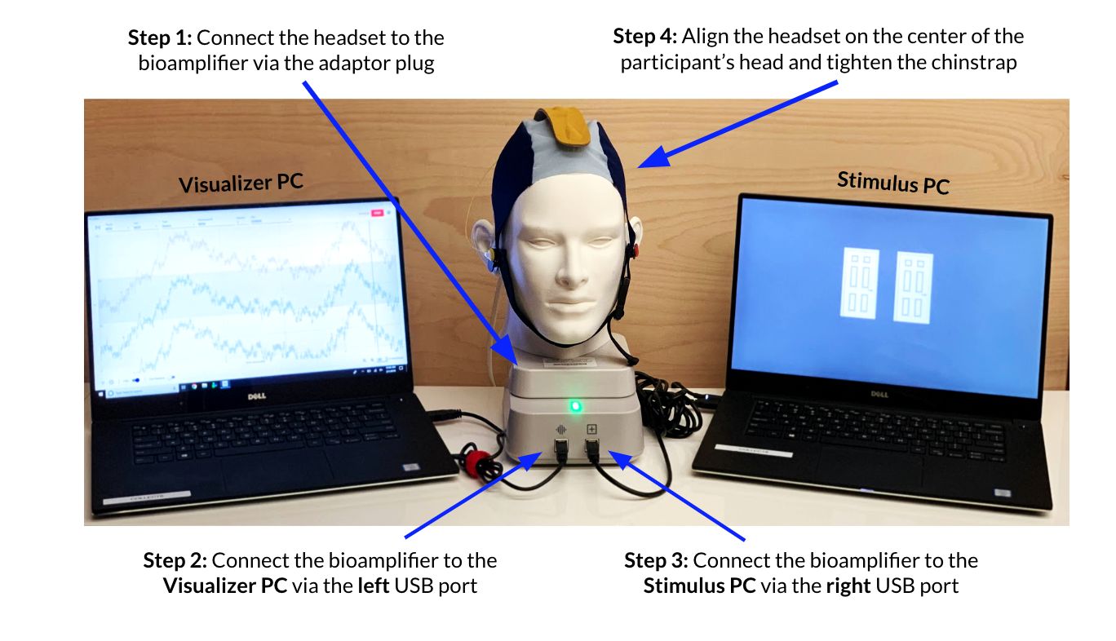
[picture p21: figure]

Figure 3: Example setup for use in Clinical Investigations.

Study Use (per participant)
1) Study staff logs into the Visualizer and Stimulus Systems.
2) Study staff places textile cap on the Participant, makes configuration settings, and verifies Visualizer software application is set up.
3) Study staff begins recording and provides a name for the recording.
4) Participant performs associated Tasks on Stimulus.
5) Study staff completes data collection and saves data.
6) Data uploaded to storage location.

Actigraphy (When available for a specific site)

1) Measurement of physical activity behaviors will be performed using accelerometry.

For Internal Use Only. This document contains confidential, proprietary information.

Document (PRD)

Rev 1

2) Prior to leaving the laboratory following completion of all testing with the M20 System, participants will be given a wrist mounted accelerometer and will be instructed to wear the accelerometer for the next 7 days.
3) Participants will be asked to only take off the accelerometer to shower and prior to aquatic activities.
4) Once the accelerometer is returned to the laboratory at the end of the 7 day period, the data will be extracted from the accelerometer via USB to the Visualizer laptop.
5) Data is then uploaded to storage location.

### 7 Requirements

The following sections identify requirements for the M20 EEG Device, herein referred to as “Product” requirements.

### 7.1 Regulatory Requirements

7.1.1 Applicable Regulations

EEG-PRD-1. The Product developed for use in clinical investigations shall comply with U.S. 21 CFR Part 812 Abbreviated Requirements and follow 21 CFR Part 820 Design Controls.
EEG-PRD-2. The device product label(s) and instructions for use shall be provided in English.

### 7.2 Requirements for the Headset and Headset Accessories (M20 3 and M20 4

Configuration)
The headset refers to the adapter and sensor strip. Headset accessories include the textile cap, sensors, and ear clips/stickers.

7.2.1 Safety and General Requirements

EEG-PRD-3. The headset and accessories in combination shall meet applicable basic electrical safety requirements per IEC 60601-1: 2012.

For Internal Use Only. This document contains confidential, proprietary information.

Document (PRD)

Rev 1

EEG-PRD-4. The headset and accessories in combination shall meet applicable electromagnetic compatibility requirements per IEC 60601-1-2 Edition 4.0 2014-02.
EEG-PRD-5. Adapter shall interface with the bioamplifier to allow the use of active sensors.
EEG-PRD-6. The surface of the adapter shall withstand cleaning by wiping down with a soft dry cloth or germicidal disposable wipe, and maintain basic safety and essential performance without damage.
EEG-PRD-7. The headset and accessories shall be designed for storage, use, and maintenance at a healthcare facility or office.
EEG-PRD-8. Adapter shall support 3 or 4 active sensors not including bias and reference signals.
EEG-PRD-9. Adapter shall mate securely to the bioamp and be removable.
EEG-PRD-10.The device shall provide 2 auxiliary connections to be attached onto each of the wearer's ears or nearby area. EEG-PRD-11.The textile cap in combination with the sensor strip shall support the placement of EEG sensors along the cranial midline at Fz, Cz, and Pz in the M20 3 configuration and at Fz, Cz, Pz, and Oz in the M20 4 configuration. Sensor placement labels are defined per International 10-20 system for placement of scalp sensors. EEG-PRD-12.Sensor strip and adapter shall protect the sensor heads and wires from damage and tangling and allow for easy assembly into the cap.
EEG-PRD-13.The sensor strip shall be made of a flexible material. EEG-PRD-14.Adapter shall incorporate bias and reference sensors. EEG-PRD-15.Connectors which attach to the sensors must penetrate hair and make contact with skin.

For Internal Use Only. This document contains confidential, proprietary information.

Document (PRD)

Rev 1

EEG-PRD-16.The device shall hold & maintain all sensor positions to enable continuous signal collection for at least 60 minutes per session.
EEG-PRD-17.The device shall transmit collected signals from its sensors to the bioamplifier.
7.2.2 Physical Requirements

EEG-PRD-18.The adapter device shall weigh no more than 1 kg. EEG-PRD-19.The adapter device shall have a physical dimension of no more than 20 cm (length) by 15 cm (width) by 6 cm (height).
EEG-PRD-20.The textile cap in combination with the sensor strip shall be lightweight and not cause discomfort when worn for at least 60 minutes.
EEG-PRD-21.The cable connecting the adapter to the bioamp shall be between 50 and 250 cm.
EEG-PRD-22.The design shall support placement and repositioning (as needed) of the headset and accessories in combination on the Participant in order to make all sensor connections.
EEG-PRD-23.The design shall support removal of the headset and accessories from the Participant in under 1 minute by the Study Staff or Participant.
EEG-PRD-24.The EEG sensors of the headset shall make contact to the Participant’s scalp through up to 20 mm of hair thickness.
EEG-PRD-25.The device shall not affect the Participant’s ability to view a computer screen and operate a keyboard, mouse and touch screen.
7.2.3 Headset Reliability and Durability Requirements

For Internal Use Only. This document contains confidential, proprietary information.

Document (PRD)

Rev 1

EEG-PRD-26.The device shall continuously operate on battery power from an attached laptop for up to 90 minutes per monitoring session.
7.2.4 Textile Cap Requirements

EEG-PRD-31.The textile cap shall fit snugly on heads ranging in size from 52 - 64 cm in such a way that the sensors make good contact with the head and don’t move around during testing.
EEG-PRD-32.The textile cap shall have holes at the correct positions to accommodate snapping in the sensor strip/adapter to read data from the desired locations on the head (both M20-3 and M20-4).
EEG-PRD-33.The textile cap shall be able to be applied on the Participant’s head in less than 3 minutes. EEG-PRD-34.The textile cap shall have a means to hold the cap on the Participant’s head.
EEG-PRD-35.The body contacting portion of the headset and accessories shall be biocompatible. EEG-PRD-36.The textile cap shall be reusable for at least 10 test sessions.
EEG-PRD-37.The textile cap shall withstand cleaning with envirocide cleaning agent as per the directions on envirocide container (at least 9 times).

### 7.3 Requirements for the Bioamplifier

7.3.1 Safety and General Requirements

EEG-PRD-38.The bioamplifier shall conform to applicable requirements of IEC-60601-2-26:2012. EEG-PRD-39.The bioamplifier shall meet applicable basic electrical safety requirements per IEC 60601-1: 2012.

For Internal Use Only. This document contains confidential, proprietary information.

Document (PRD)

Rev 1

EEG-PRD-40.The bioamplifier shall meet applicable electromagnetic compatibility requirements per 60601-1-2 Edition 4.0 2014-02.
EEG-PRD-41.EEG system should sample data of waveforms from .1 -75 Hz.
EEG-PRD-42.The bioamplifier shall sample input EEG signals at a minimum frequency of 100Hz for digitization. EEG-PRD-43.The bioamplifier shall have 2 USB type B interfaces. EEG-PRD-44.The bioamplifier shall be powered by isolated low voltage (5 VDC) supply.
EEG-PRD-45.The bioamplifier sensor input shall have a high impedance suitable for dry sensors (passive or active sensors).
EEG-PRD-46.The adapter shall plug into the bioamplifier. EEG-PRD-47.The bioamplifier shall be designed for storage, use, and maintenance at a healthcare facility or office. EEG-PRD-48.The bioamplifier shall provide a visual indication for the power on condition.
EEG-PRD-49.The bioamplifier shall be powered from a connected computer.
EEG-PRD-50.The bioamplifier shall continuously operate on battery power supplied by an attached laptop for up to 90 minutes per monitoring session.
7.3.2 Physical Requirements

EEG-PRD-51.The bioamplifier shall weigh no more than 1 kg. EEG-PRD-52.The bioamplifier shall have a physical dimension of no more than 20 cm (length) by 15 cm (width) by 10 cm (height).
7.3.3 Bioamplifier Packaging and Labeling Requirements

For Internal Use Only. This document contains confidential, proprietary information.

Document (PRD)

Rev 1

EEG-PRD-53.The bioamplifier shall have a product label containing product and regulatory information. EEG-PRD-54.The bioamplifier shall have an Instructions for Use (IFU). 7.3.4 Bioamp Firmware Requirements

EEG-PRD-55.The bioamplifier shall be configurable to support 32 channels of EEG signals.
EEG-PRD-56.The bioamp firmware shall consolidate the stimulus mark data received from the Stimulus Software with the received EEG waveform data.
EEG-PRD-57.The bioamplifier shall support receipt of stimulus marks via a USB interface.
EEG-PRD-58.The bioamplifier shall support transmission of digitized EEG signals and stimulus marks to a connected computer via a USB type B interface. EEG-PRD-59.The bioamp firmware shall process received EEG waveform data.
EEG-PRD-60.The bioamp firmware shall process test initialization from the Visualizer System.
EEG-PRD-61.The bioamp firmware shall generate consolidated EEG waveform and stimulus mark data. EEG-PRD-62.The bioamp firmware shall configure the bioamplifier based on received configuration parameters. EEG-PRD-63.The bioamplifier shall support a command line interface via a USB interface.

### 7.4 Requirements for the Visualizer System (Collect Software and Installed

Computer)
7.4.1 Hardware Requirements

EEG-PRD-64.The Visualizer System shall allow a standalone execution of the Collect software.

For Internal Use Only. This document contains confidential, proprietary information.

Document (PRD)

Rev 1

EEG-PRD-65.The Visualizer System shall allow utilization of a mouse connected via USB for navigation and selection. EEG-PRD-66.The Visualizer System shall connect and integrate to the bioamp via a USB port.
EEG-PRD-67.The Visualizer System shall allow utilization of a keyboard to manage the entering of selections and management of the device.
EEG-PRD-68.The Visualizer System shall allow for continuous collection of EEG signals on battery power for at least 90 minutes without requiring recharging.
EEG-PRD-69.The Visualizer System shall communicate via USB to an Actigraphy sensor.
EEG-PRD-70.The Visualizer System shall allow automatic setting of the port connected to the bioamp. EEG-PRD-71.The Visualizer system shall allow at least 100 GB of storage space.
EEG-PRD-72.The Visualizer system shall allow at least 8GB of RAM. 7.4.2 Configuration Requirements

EEG-PRD-73.The Visualizer System hard disk or other local storage shall be encrypted.
EEG-PRD-74.The Collect Software shall load default configuration settings at startup.
EEG-PRD-75.The Collect Software shall allow the loading of the last set of configuration settings.
EEG-PRD-76.The Collect Software shall allow the saving of configuration settings to the application root directory. EEG-PRD-77.The Visualizer System shall use the login for the Windows Operating System.
EEG-PRD-78.The Visualizer System shall allow Administration login for the Windows Operating System.

For Internal Use Only. This document contains confidential, proprietary information.

Document (PRD)

Rev 1

EEG-PRD-79.The Visualizer System shall have a “break glass” account with administrator privileges. EEG-PRD-80.The Visualizer System shall allow the setting of the Windows Operating System date time. EEG-PRD-81.The Visualizer System shall allow a user to modify the configuration file associated with the Collect software. EEG-PRD-82.The Visualizer System shall allow a user to modify the configuration of the Collect software through the Collect software user interface.
EEG-PRD-83.The Collect Software shall display the bioamp firmware version.
7.4.3 Visualizer System Setup

EEG-PRD-84.The Visualizer System shall be setup with a desktop icon for selection to initiate the software application. EEG-PRD-85.The Visualizer System shall allow privileges for the Collect Software application to read, write, delete, and execute within the installed Visualizer Software application directory.
EEG-PRD-86.The Visualizer System shall allow access to the internet for upload to storage.
EEG-PRD-87.The Visualizer System shall lock the user interface after 60 min of inactivity.
7.4.4 Collect Software Initialization

EEG-PRD-88.The Collect Software shall maximize the screen when executing the software application.
EEG-PRD-89.The Collect Software shall allow sending a test message to the connecting bioamp when initiated and receive the ack response (or no response). (On start up only) EEG-PRD-90.The Collect Software shall display errors when encountering processing or communication errors.

For Internal Use Only. This document contains confidential, proprietary information.

Document (PRD)

Rev 1

EEG-PRD-91.The Collect Software shall allow the display of an error message if the configuration file is not accessible during initiation or the system does not have access privileges. 7.4.5 Collect Software User Interface Requirements

EEG-PRD-92.The Collect Software shall allow the selection of the Bioamplifier Serial Port.
EEG-PRD-93.The Collect Software shall allow the display of a Start Recording option.
EEG-PRD-94.The Collect Software shall allow the display of a Stop Recording option.
EEG-PRD-95.The Collect Software shall allow the display of a file save location.
EEG-PRD-96.The Collect Software shall allow the display of a Start Filter display option.
EEG-PRD-97.The Collect Software shall allow the display of a Session Preset configuration list selection. EEG-PRD-98.The Collect Software shall allow the display of a Serial Port configuration list selection. EEG-PRD-99.The Collect Software shall allow the display of the set date / time.
EEG-PRD-100. The Collect Software shall allow the display of the current logged in user and include the current logged in user in the EEG file produced.
EEG-PRD-101. The Collect Software shall allow the display of the current session.
EEG-PRD-102. | The Collect Software shall allow the display of the current EEG Waveform data.
EEG-PRD-103. | The Collect Software shall allow the setting of the current Participant ID.

For Internal Use Only. This document contains confidential, proprietary information.

Document (PRD)

Rev 1

EEG-PRD-104. | The Collect Software shall allow the setting of the current Task being executed from the Stimulus System.
EEG-PRD-105. | The Collect Software shall allow the setting of the current clinical site.
EEG-PRD-106. | The Collect Software shall provide separate view options for the waveform display.
EEG-PRD-107. | The Collect Software shall display each sensor identified on the waveform display.
EEG-PRD-108. | The Collect Software shall display the update waveform display moving left to right.
EEG-PRD-109. | The Collect Software shall allow setting of the interval scale for display updates.
EEG-PRD-110. | The Collect Software shall allow both horizontal Time and Frequency display options.
EEG-PRD-111. | The Collect Software shall allow vertical µV (microvolt) vertical display adjustment.
EEG-PRD-112. | The Collect Software shall display Mark data sent from the Stimulus System.
EEG-PRD-113. | The Collect Software shall allow the display of a configuration view.
EEG-PRD-114. | The Collect Software shall display of the current date/ time on the Visualizer system.
EEG-PRD-115. | The Collect Software shall display a popup for entering a unique recording name.
EEG-PRD-116. | The Collect Software shall display the current software version.

7.4.6 Visualizer - Bioamp Interface

EEG-PRD-117. The Collect Software shall allow the display of the Serial Port connection to the Bioamplifier.

For Internal Use Only. This document contains confidential, proprietary information.

Document (PRD)

Rev 1

EEG-PRD-118. | The Visualizer System shall allow the Collect Software application to place the Bioamplifier into Test mode.
EEG-PRD-119. | The Visualizer System shall allow the Collect Software application to set the Bioamplifier current channel configuration.
EEG-PRD-120. | The Visualizer System shall allow the Bioamplifier to send the EEG data to the Collect Software application.
EEG-PRD-121. | The Visualizer System shall allow the Bioamplifier to send the Stimulus mark data to the Collect Software application.

7.4.7 Visualizer - Actigraphy Interface

EEG-PRD-122. | The Visualizer System shall allow connection of an Actigraphy device.
EEG-PRD-123. | The Visualizer System shall allow passing of Actigraphy data to data storage.
EEG-PRD-124. | The Visualizer System shall allow execution of a Actigraphy application software with required security controls in place.
EEG-PRD-125. | The Visualizer System shall allow temporary storage of received Actigraphy data

7.4.8 Additional Visualizer Requirements

EEG-PRD-126. | The Collect Software shall allow saving of data to a log file stored in the executable root directory.
EEG-PRD-127. | The Collect Software shall allow output to data storage a file for recorded data from sensors.
EEG-PRD-128. | The Collect Software shall allow output to data storage a file for the metadata associated with the recorded data configuration parameters.

For Internal Use Only. This document contains confidential, proprietary information.

Document (PRD)

Rev 1

7.4.9 Non-functional Requirements for the Collect Software

7.4.9.1 | Serviceability / Maintainability
EEG-PRD-129. | The Collect Software shall allow retaining all
existing configuration settings during upgrade and (re)installation of the Collect Software application.

Revision History
Rev | Description of Change | Effective Date
1 | Initial Release

For Internal Use Only. This document contains confidential, proprietary information.

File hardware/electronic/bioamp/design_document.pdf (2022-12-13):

# M20 EE Design Document

M20 bioamplifier is a 32 channel EEG project developed by Philo. It is designed to be connected to a PC USB port for data communication.

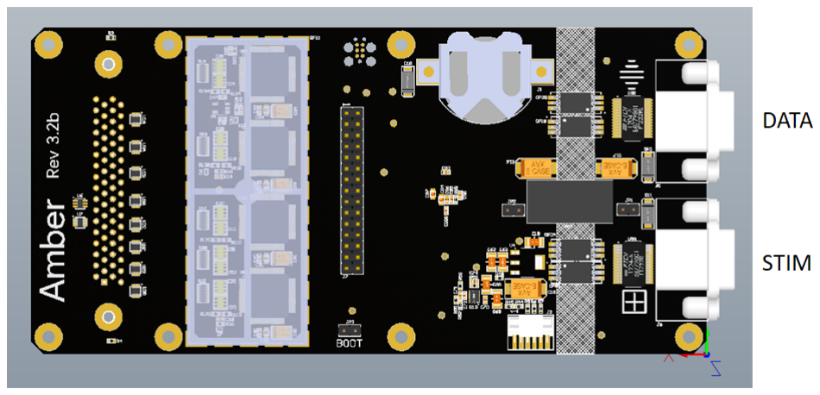
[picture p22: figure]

### 1. Hardware Design

### 1.1. DAQ

The heart of the design is the ADS1299 8 channel bioamplifier from Texas Instruments. This single IC provides the front-end amplification and 24 bit conversion. It is particularly suitable for EEG measurements as it provides a ground bias generator and built-in lead-off detection.

4 of the ADS1299s are connected together in a parallel data configuration. All 4 together provide 32 EEG channels. U1A is the master ADS1299 and provides the conversion clock to the other 3 converters to keep things synchronized. U1A is also the master bias generator.

Although the ADS1299 can provide differential or single-ended inputs, the configuration of the board allows for only single-ended inputs on channels 1-24, and the option of single-ended or differential inputs on channels 25-32.

The sample rate is 250 samples per second.

Communication with the MCU is over 4 wire SPI running at a clock speed of 4 MHz. The ADS1299 provides a signal (#DRDY) that goes low when a conversion is ready to be read out of the chip. Only the master has this signal connected to the MCU and as all timing is referenced to it. Individual chip selects are asserted to read the data from each of the ADS1299s in turn. An alternate option would be to ready the data in a daisy-chain configuration, but the parallel configuration was chosen for its speed and flexibility.

### 1.2. MCU

The MCU is a Kinetis (NXP/Freescale) KL27Z256 in a 64 pin QFP package. This is an Arm Cortex M0 processor running at 48 MHz with 256K of flash memory. The reasons for choosing this processor include the speed, cost, availability, and ease of development with the Kinetis tool chain.

Debugging is done through a dedicated JTAG port implemented with a special TAG connect cable. Production programming is done through the DATA USB port utilizing the built-in ROM bootloader and a special Python tool.

The MCU handles the data conversion from the ADS1299s and communication with the host PC. It is also responsible for monitoring the on-board power supplies.

4 input pins allow for identifying the hardware revision through pull-down resistors. 4 pins are also reserved for future expansion.

Although the MCU has low-power modes, in this design it is always running at full power.

### 1.3. Power Supplies

Power to the board comes from either one of the 2 USB connectors. USB voltage is diode-ORed and powers an isolated DC/DC converter (PS1). This provides the 4kv isolation and patient leakage current protection. Jumpers JP1 and JP2 must be installed for normal operation. These were implement to provide power flexibility in the event a battery would need to be used.

The 5V output of the DC/DC converter is linear regulated down to 3.3V. A linear regulated was chosen to provide a lower noise floor than another DC/DC. The 3.3V primary powers the MCU and digital logic.

A charge pump based converter also runs off the 3.3V rail and provides the +/-2.5V rails to the ADS1299s. Normally charge pumps are rather noisy, but this particular IC (LM27762) has built-in linear regulators following the charge pumps and is tailored to these sorts of applications.

A separate 2.5V reference is also generated to power the MCU analog section and to provide a precise reference for power supply measurements.

### 1.4. USB Ports

Two USB ports connect the PCB to a PC. The DATA port is used to transfer the streaming EEG data. The STIM port allows control of the board and is used to set marks in the EEG data stream.

Each port uses an FTDI232 USB to serial IC on the PC side. The MCU side implements optical isolators for patient protection. These are rated at 4kv with a maximum data rate of 10Mbps.

### 1.5. Real Time Clock

A real time clock is implemented. It communicates over I2C with the MCU and has battery backup.

### 1.6. Micro SD

A micro SD slot is provided for future expansion. It is connected to a second SPI port on the MCU.

### 1.7. Expansion/Debug Header

Board test and expansion signals are brought to this header. They are labeled in the layout and provide an easy means of testing or debugging the board.

### 2. Layout

The PCB is designed as a 6 layer board. The layer stack is signal, ground plane, signal, signal, power connections, signal. Minimum line/space is 6/6 and minimum via size is 6/16. Board material is plain FR4 and finish is ENIG. This is standard for today’s fabrication processes and allows the board to be manufactured at any number of board houses.

The board is separated into 3 distinct sections: PC non-isolated, digital, and analog.

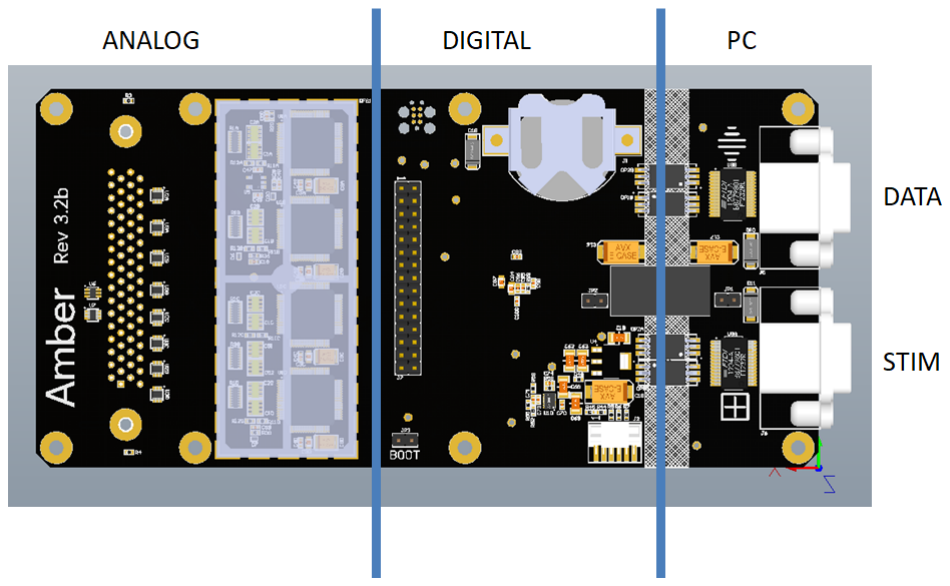
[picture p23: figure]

### 2.1. PC

The PC side has the USB ports and half the optical isolators and DC/DC converter. Creepage and clearance is maintained at 8mm.

### 2.2. Digital

The digital section incorporates the power supplies and MCU. The expansion header is also included here.

### 2.3. Analog

The analog section protects the microvolt level EEG signals from the noisy digital sections. An RF shield is included that encapsulates the ADS1299 converters. A split ground plane separates the sensitive ground returns from the noisy digital grounds:


### 2.4. Test Points

Various individual test points are provided as well as the debug header for future automated testing.

### 3. Firmware

The firmware was developed in C using the Kinetis Design Studio. Some functions were developed with the help of Kinetis’s Processor Expert which simplifies MCU configuration parameters. Some low-level drivers were hand written for the high performance and low latency needed processing the EEG data.

A main loop handles gathering EEG data, doing serial communication, and blinking LEDs. Some tasks are event driven such as EEG data ready and serial communication. These typically either buffer the data or raise flags for processing in the main loop.

A text based command line interpreter (CLI) is implemented for easy control and communication. Any terminal program can be used for sending commands. Although the CLI will respond to commands from either port, only characters on the STIM port are echoed. CLI responses on the DATA port are multiplexed with the streaming EEG data by prefixing ‘CLI:’ to the response line. Commands to the CLI are terminated by a carriage return.

EEG data is continuously streamed on the DATA port in ASCII format. Each channel is comma separated and the EEG value is encoded as a signed 24 bit value. A frame of EEG data has the following format:

SEQUENCE NUMBER | CH 1 | CH 2 | … | CH32 | MARK | CR/LF

The frame is prefixed by ‘DATA:’. The sequence number is an auto incrementing unsigned 32 bit value. The mark is a user-selected data value appended to the EEG stream. Each line is terminated by a carriage return/line feed.

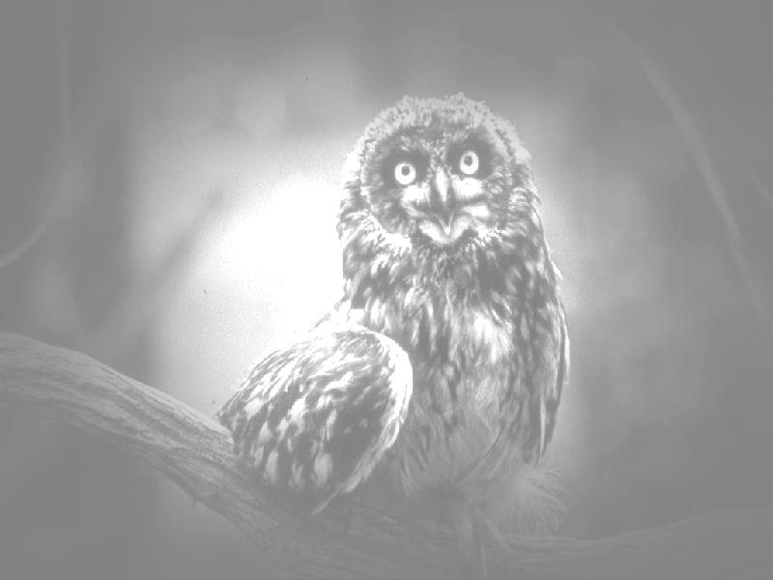
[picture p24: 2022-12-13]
stimulus/resources/emotional_images/neutral_animals/5_neutaml.jpg

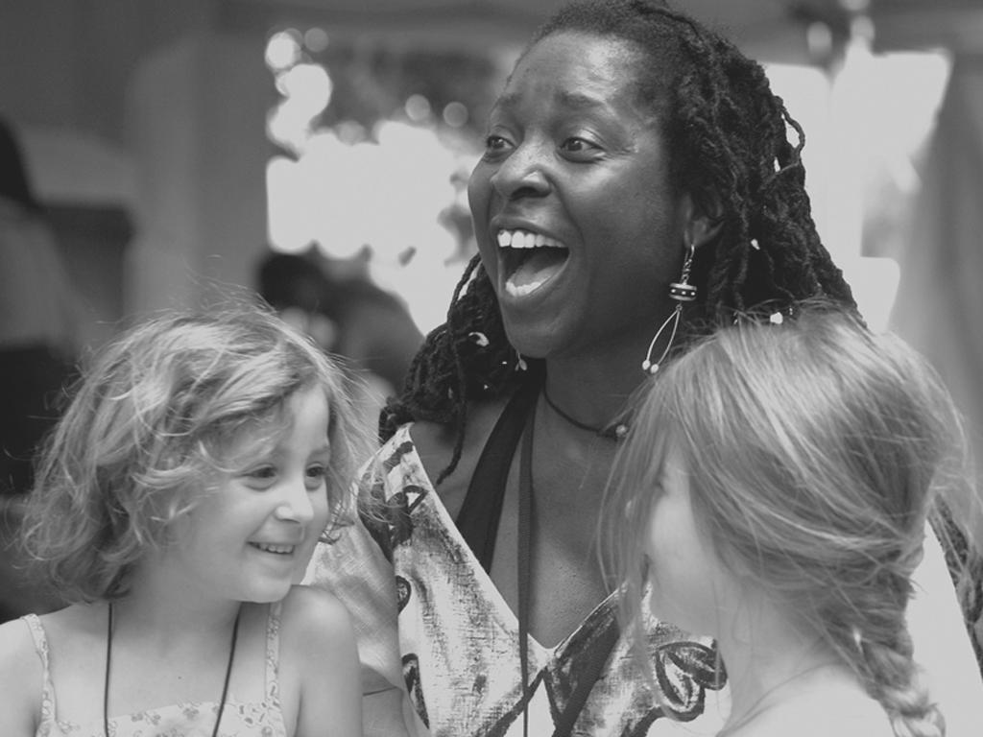
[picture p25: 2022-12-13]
stimulus/resources/ssvep/pleasant/12_pleasant.jpg

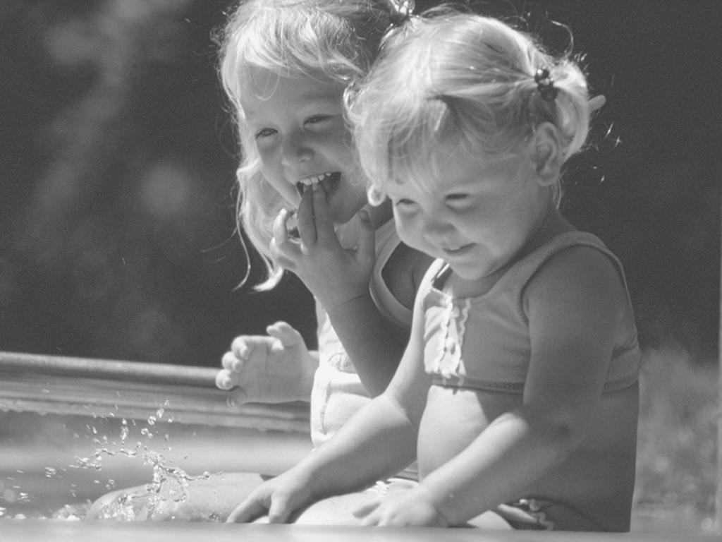
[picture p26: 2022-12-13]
stimulus/resources/ssvep/pleasant/8_pleasant.jpg

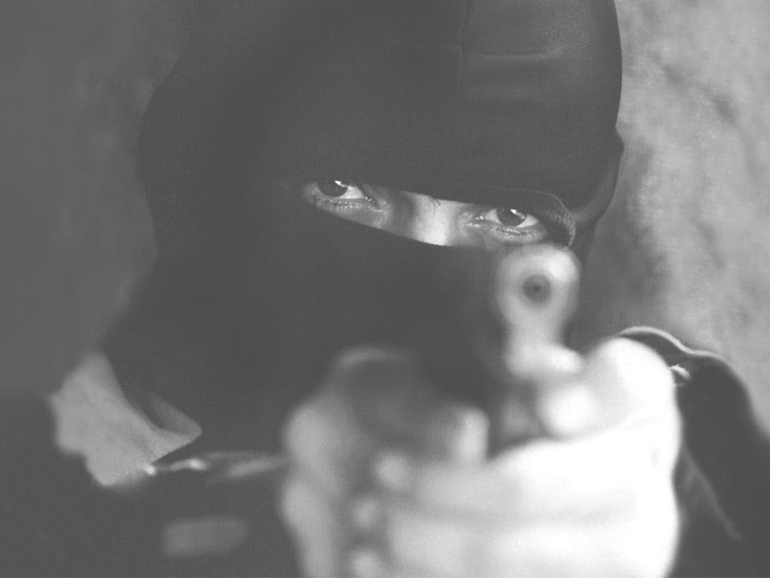
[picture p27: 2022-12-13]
stimulus/resources/ssvep/unpleasant/23_unpleasant.jpg

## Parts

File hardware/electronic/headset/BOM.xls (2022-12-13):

Level | Part Number | Part Type | Description | Lifecycle Phase | Commodity Code | Rev | Rev Incorp Date | Rev Release Date | Effectivity Date | Shippable Item | Exclude from Rollup | Overall Compliance | Compliance Calculated Date | Mass | Mass-measure | Product Line(s) | Thumbnail | Sites | BOM.Thumbnail | BOM.Item Type | BOM.Item Description | BOM.Item Rev | BOM.Item Lifecycle Phase | BOM.Qty | BOM.UOM | BOM.Find Num | BOM.Ref Des | BOM.Organization | BOM.Usergroup Access - External | BOM.Legacy Item Number | BOM.OK to Purchase | BOM.Substitute | BOM.BOM Notes | BOM.Summary Compliance | BOM.Identifier | BOM.CAD Filename | BOM.Component | BOM.Reference | BOM.Publish Source | Manufacturers.Mfr. Name | Manufacturers.Mfr. Part Number | Manufacturers.Mfr. Part Description | Manufacturers.Mfr Class | Manufacturers.Mfr. Part Lifecycle Phase | Manufacturers.Preferred Status | Manufacturers.Qualification Status | Manufacturers.Reference Notes | Manufacturers.Summary Compliance | Manufacturers.Smelters | Manufacturers.Conflict Mineral Status
0 | 650-02489-01 | 650-PCBA | PCBA, A.E BREAKOUT, REV 3.1, AMBER | Prototype | ASSY.PCBA | 01 MCO-006790 | 05/21/2019 10:09:44 AM PDT | 06/19/2019 02:34:10 PM PDT |  | Yes | No |  |  |  |  | AMBER |  |  |  |  |  |  |  |  |  |  |  |  |  |  |  |  |  |  |  |  |  |  |  | GORILLA CIRCUITS | 650-02489-01 | PCBA, A.E BREAKOUT, REV 3.1, AMBER | non-disti | Active | Preferred
1 | 150-03851-00 | 150-Capacitor | CAP, CER, X7R, 0.1UF, 10%, 50V, 0805, AMBER | Production | COMP.CAPACITOR | A MCO-006791 | 03/28/2019 04:22:29 AM PDT | 06/19/2019 02:22:10 PM PDT |  | Yes | No |  |  |  |  | AMBER |  |  |  | 150-Capacitor | CAP, CER, X7R, 0.1UF, 10%, 50V, 0805, AMBER | A MCO-006791 | Production | 20 | Each | 0 | C1A,C3A,C5A,C7A,C1B,C3B,C5B,C7B,C1C,C3C,C5C,C7C,C1D,C3D,C5D,C7D,C1E,C3E,C5E,C7E | ORG - AMB |  |  |  |  |  |  |  |  |  |  |  | AVX | 08055C104KAT2A | CAP, CER, X7R, 0.1UF, 10%, 50V, 0805 | non-disti | Active | Preferred |  |  | Non-Compliant | Gejiu Non-Ferrous Metal Processing Co., Ltd. - [Tin];PT Bukit Timah - [Tin];PT Refined Bangka Tin - [Tin];PT Timah (Persero) Tbk Mentok - [Tin];Thaisarco - [Tin];Aida Chemical Industries Co., Ltd. - [Gold];Allgemeine Gold-und Silberscheideanstalt A.G. - [Gold];AngloGold Ashanti Córrego do Sítio Mineração - [Gold];Argor-Heraeus S.A. - [Gold];Asahi Pretec Corp. - [Gold];Asaka Riken Co., Ltd. - [Gold];PT Bangka Prima Tin - [Tin];PT Sukses Inti Makmur - [Tin];A.L.M.T. TUNGSTEN Corp. - [Tungsten];Kennametal Huntsville - [Tungsten];Chongyi Zhangyuan Tungsten Co., Ltd. - [Tungsten];Aurubis AG - [Gold];Bangko Sentral ng Pilipinas (Central Bank of the Philippines) - [Gold];Boliden AB - [Gold];C. Hafner GmbH + Co. KG - [Gold];CCR Refinery - Glencore Canada Corporation - [Gold];Chimet S.p.A. - [Gold];Dowa - [Gold];Heimerle + Meule GmbH - [Gold];Heraeus Metals Hong Kong Ltd. - [Gold];Heraeus Precious Metals GmbH & Co. KG - [Gold];Ishifuku Metal Industry Co., Ltd. - [Gold];Istanbul Gold Refinery - [Gold];Asahi Refining USA Inc. - [Gold];Asahi Refining Canada Ltd. - [Gold];JX Nippon Mining & Metals Co., Ltd. - [Gold];Kennecott Utah Copper LLC - [Gold];Kojima Chemicals Co., Ltd. - [Gold];LS-NIKKO Copper Inc. - [Gold];Materion - [Gold];Matsuda Sangyo Co., Ltd. - [Gold];Metalor Technologies (Hong Kong) Ltd. - [Gold];Metalor Technologies S.A. - [Gold];Metalor USA Refining Corporation - [Gold];Metalúrgica Met-Mex Peñoles S.A. De C.V. - [Gold];Mitsubishi Materials Corporation - [Gold];Mitsui M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 | Non-Compliant
1 | 150-03852-00 | 150-Capacitor | CAP, CER, X5R, 2.2UF, 20%, 10V, 0805, AMBER | Production | COMP.CAPACITOR | A MCO-006791 | 03/28/2019 04:22:29 AM PDT | 06/19/2019 02:22:10 PM PDT |  | Yes | No |  |  |  |  | AMBER |  |  |  | 150-Capacitor | CAP, CER, X5R, 2.2UF, 20%, 10V, 0805, AMBER | A MCO-006791 | Production | 10 | Each | 0 | C2A,C6A,C2B,C6B,C2C,C6C,C2D,C6D,C2E,C6E | ORG - AMB |  |  |  |  |  |  |  |  |  |  |  | YAGEO | CC0805MRX5R6BB225 | CAP, CER, X5R, 2.2UF, 20%, 10V, 0805 | non-disti | Active | Preferred |  |  | Compliant | Malaysia Smelting Corporation (MSC) - [Tin] | Compliant
1 | 150-03853-00 | 150-Capacitor | CAP, CER, X7R, 3.3UF, 10%, 16V, 0805, AMBER | Production | COMP.CAPACITOR | A MCO-006791 | 03/28/2019 04:22:29 AM PDT | 06/19/2019 02:22:10 PM PDT |  | Yes | No |  |  |  |  | AMBER |  |  |  | 150-Capacitor | CAP, CER, X7R, 3.3UF, 10%, 16V, 0805, AMBER | A MCO-006791 | Production | 10 | Each | 0 | C4A,C8A,C4B,C8B,C4C,C8C,C4D,C8D,C4E,C8E | ORG - AMB |  |  |  |  |  |  |  |  |  |  |  | TDK | CGA4J3X7R1C335K125AB | CAP, CER, X7R, 3.3UF, 10%, 16V, 0805 | non-disti | Active | Preferred |  |  | Missing Info | Malaysia Smelting Corporation (MSC) - [Tin] | Missing Info
1 | 210-04159-00 | 210-Connector | CONN, JACK, THREADED, 1MM, 12.7MM H, GOLD, PANEL MOUNT, AMBER | Production | COMP.CAPACITOR | A MCO-006791 | 03/28/2019 04:22:29 AM PDT | 06/19/2019 02:22:10 PM PDT |  | Yes | No |  |  |  |  | AMBER |  |  |  | 210-Connector | CONN, JACK, THREADED, 1MM, 12.7MM H, GOLD, PANEL MOUNT, AMBER | A MCO-006791 | Production | 5 | Each | 0 | J1,J3,J4,J11,J12 | ORG - AMB |  |  |  |  |  |  |  |  |  |  |  | Plastic Dip International | 38255 | CONN, JACK, THREADED, 1MM, 12.7MM H, GOLD, PANEL MOUNT | non-disti | Active | Preferred |  |  | Missing Info | Malaysia Smelting Corporation (MSC) - [Tin] | Missing Info
1 | 210-04160-00 | 210-Connector | CONN, D-CAP, PLUG, VERT, 2x34, 1.27MM P, 9..3MM H, GOLD, TH, AMBER | Production | COMP.CAPACITOR | A MCO-006791 | 03/28/2019 04:22:29 AM PDT | 06/19/2019 02:22:10 PM PDT |  | Yes | No |  |  |  |  | AMBER |  |  |  | 210-Connector | CONN, D-CAP, PLUG, VERT, 2x34, 1.27MM P, 9..3MM H, GOLD, TH, AMBER | A MCO-006791 | Production | 1 | Each | 0 | J2 | ORG - AMB |  |  |  |  |  |  |  |  |  |  |  | TE CONNECTIVITY | 2-5174339-5 | CONN, D-CAP, VERT, 2x34, 1.27MM P, 9..3MM H, GOLD, TH | non-disti | Active | Preferred |  |  | Missing Info |  | Exempt
1 | 313-05186-00 | 313-IC | IC, CURRENT SOURCE, SINK MIRROR, ±0.25% ACCURATE, 2.5 TO 40 VIN, 100UA OUT, SOIC-8, AMBER | Production | COMP.CAPACITOR | A MCO-006791 | 03/28/2019 04:22:29 AM PDT | 06/19/2019 02:22:10 PM PDT |  | Yes | No |  |  |  |  | AMBER |  |  |  | 313-IC | IC, CURRENT SOURCE, SINK MIRROR, ±0.25% ACCURATE, 2.5 TO 40 VIN, 100UA OUT, SOIC-8, AMBER | A MCO-006791 | Production | 5 | Each | 0 | U1A,U1B,U1C,U1D,U1E | ORG - AMB |  |  |  |  |  |  |  |  |  |  |  | TEXAS INSTRUMENTS INC | REF200AU/2K5 | IC, CURRENT SOURCE, SINK MIRROR, ±0.25% ACCURATE, 2.5 TO 40 VIN, 100UA OUT, SOIC-8 | non-disti | Active | Preferred |  |  | Non-Compliant | Aurubis AG - [Gold];Bangko Sentral ng Pilipinas (Central Bank of the Philippines) - [Gold];Boliden AB - [Gold];C. Hafner GmbH + Co. KG - [Gold];CCR Refinery - Glencore Canada Corporation - [Gold];Chimet S.p.A. - [Gold];Dowa - [Gold];Elemetal Refining, LLC - [Gold];Heimerle + Meule GmbH - [Gold];Heraeus Metals Hong Kong Ltd. - [Gold];Heraeus Precious Metals GmbH & Co. KG - [Gold];JX Nippon Mining & Metals Co., Ltd. - [Gold];Kennecott Utah Copper LLC - [Gold];Ishifuku Metal Industry Co., Ltd. - [Gold];Istanbul Gold Refinery - [Gold];Kojima Chemicals Co., Ltd. - [Gold];LS-NIKKO Copper Inc. - [Gold];Materion - [Gold];Matsuda Sangyo Co., Ltd. - [Gold];Metalor Technologies (Hong Kong) Ltd. - [Gold];Metalor Technologies S.A. - [Gold];Metalor USA Refining Corporation - [Gold];Metalúrgica Met-Mex Peñoles S.A. De C.V. - [Gold];Mitsubishi Materials Corporation - [Gold];Mitsui Mining and Smelting Co., Ltd. - [Gold];Nihon Material Co., Ltd. - [Gold];Ohura Precious Metal Industry Co., Ltd. - [Gold];PAMP S.A. - [Gold];Republic Metals Corporation - [Gold];Royal Canadian Mint - [Gold];SEMPSA Joyería Platería S.A. - [Gold];Shandong Zhaojin Gold & Silver Refinery Co., Ltd. - [Gold];Solar Applied Materials Technology Corp. - [Gold];Sumitomo Metal Mining Co., Ltd. - [Gold];Tanaka Kikinzoku Kogyo K.K. - [Gold];Tokuriki Honten Co., Ltd. - [Gold];Umicore Precious Metals Thailand - [Gold];Umicore SA Business Unit Precious Metals Refining - [Gold];United Precious Metal Refining, Inc. - [Gold];Wester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 | Non-Compliant
1 | 313-05187-00 | 313-IC | IC, OPAMP, OPA333, RAIL-TO-RAIL, 1.8 TO 5.5 VIN SINGLE, 0.9 TO 2.75 VIN DUAL, 350KHZ, SOT23-5, AMBER | Production | COMP.CAPACITOR | A MCO-006791 | 03/28/2019 04:22:29 AM PDT | 06/19/2019 02:22:10 PM PDT |  | Yes | No |  |  |  |  | AMBER |  |  |  | 313-IC | IC, OPAMP, OPA333, RAIL-TO-RAIL, 1.8 TO 5.5 VIN SINGLE, 0.9 TO 2.75 VIN DUAL, 350KHZ, SOT23-5, AMBER | A MCO-006791 | Production | 10 | Each | 0 | U2A,U3A,U2B,U3B,U2C,U3C,U2D,U3D,U2E,U3E | ORG - AMB |  |  |  |  |  |  |  |  |  |  |  | TEXAS INSTRUMENTS INC | OPA333AIDBVR | IC, OPAMP, OPA333, RAIL-TO-RAIL, 1.8 TO 5.5 VIN SINGLE, 0.9 TO 2.75 VIN DUAL, 350KHZ, SOT23-5 | non-disti | Active | Preferred |  |  | Non-Compliant | Aurubis AG - [Gold];BANGALORE REFINERY - [GOLD];Bangko Sentral ng Pilipinas (Central Bank of the Philippines) - [Gold];Boliden AB - [Gold];C. Hafner GmbH + Co. KG - [Gold];Caridad - [Gold];CCR Refinery - Glencore Canada Corporation - [Gold];Cendres + Métaux S.A. - [Gold];Chimet S.p.A. - [Gold];Chugai Mining - [Gold];Daejin Indus Co., Ltd. - [Gold];Daye Non-Ferrous Metals Mining Ltd. - [Gold];DODUCO GmbH - [Gold];Dowa - [Gold];DSC (Do Sung Corporation) - [Gold];Eco-System Recycling Co., Ltd. - [Gold];Elemetal Refining, LLC - [Gold];Emirates Gold DMCC - [Gold];Gansu Seemine Material Hi-Tech Co., Ltd. - [Gold];Geib Refining Corporation - [Gold];Great Wall Precious Metals Co., LTD. of CBPM - [Gold];Guangdong Jinding Gold Limited - [Gold];GUJARAT GOLD CENTRE - [GOLD];Guoda Safina High-Tech Environmental Refinery Co., Ltd. - [Gold];Hangzhou Fuchunjiang Smelting Co., Ltd. - [Gold];Heimerle + Meule GmbH - [Gold];Heraeus Metals Hong Kong Ltd. - [Gold];Heraeus Precious Metals GmbH & Co. KG - [Gold];Hunan Chenzhou Mining Co., Ltd. - [Gold];HwaSeong CJ CO., LTD. - [Gold];Jiangxi Copper Co., Ltd. - [Gold];JSC Ekaterinburg Non-Ferrous Metal Processing Plant - [Gold];JSC Uralelectromed - [Gold];JX Nippon Mining & Metals Co., Ltd. - [Gold];Kaloti Precious Metals - [Gold];Kazakhmys Smelting LLC - [Gold];Kazzinc - [Gold];Kennecott Utah Copper LLC - [Gold];KGHM Polska Mied? Spó?ka Akcyjna - [Gold];Inner Mongolia Qiankun Gold and Silver Refinery Share Co., Ltd. - [Gold];Ishifuku Metal Industry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 | Non-Compliant
1 | 470-16940-00 | 470-Resistor | RES, 1.18K, 1%, 1/8W, 0805, AMBER | Production | COMP.CAPACITOR | A MCO-006790 | 03/28/2019 04:22:30 AM PDT | 06/19/2019 02:34:10 PM PDT |  | Yes | No |  |  |  |  | AMBER |  |  |  | 470-Resistor | RES, 1.18K, 1%, 1/8W, 0805, AMBER | A MCO-006790 | Production | 10 | Each | 0 | R1A,R4A,R1B,R4B,R1C,R4C,R1D,R4D,R1E,R4E | ORG - AMB |  |  |  |  |  |  |  |  |  |  |  | YAGEO | RC0805FR-071K18L | RES, 1.18K, 1%, 1/8W, 0805 | non-disti | Active | Preferred |  |  | Missing Info
1 | 470-16941-00 | 470-Resistor | RES, 680K, 1%, 1/8W, 0805, AUTO GRADE, AMBER | Production | COMP.CAPACITOR | A MCO-006790 | 03/28/2019 04:22:30 AM PDT | 06/19/2019 02:34:10 PM PDT |  | Yes | No |  |  |  |  | AMBER |  |  |  | 470-Resistor | RES, 680K, 1%, 1/8W, 0805, AUTO GRADE, AMBER | A MCO-006790 | Production | 10 | Each | 0 | R2A,R5A,R2B,R5B,R2C,R5C,R2D,R5D,R2E,R5E | ORG - AMB |  |  |  |  |  |  |  |  |  |  |  | PANASONIC | ERJ-6ENF6803V | RES, 680K, 1%, 1/8W, 0805, AUTO GRADE | non-disti | Active | Preferred |  |  | Missing Info | Malaysia Smelting Corporation (MSC) - [Tin] | Missing Info
1 | 470-16942-00 | 470-Resistor | RES, JUMPER, 0, 1/8W, 0805, AUTO GRADE, AMBER | Production | COMP.CAPACITOR | A MCO-006790 | 03/28/2019 04:22:30 AM PDT | 06/19/2019 02:34:10 PM PDT |  | Yes | No |  |  |  |  | AMBER |  |  |  | 470-Resistor | RES, JUMPER, 0, 1/8W, 0805, AUTO GRADE, AMBER | A MCO-006790 | Production | 10 | Each | 0 | R3A,R6A,R3B,R6B,R3C,R6C,R3D,R6D,R3E,R6E | ORG - AMB |  |  |  |  |  |  |  |  |  |  |  | PANASONIC | ERJ-6GEY0R00V | RES, JUMPER, 0, 1/8W, 0805, AUTO GRADE | non-disti | Active | Preferred |  |  | Missing Info | PT Timah (Persero) Tbk Mentok - [Tin];PT Bukit Timah - [Tin];PT Refined Bangka Tin - [Tin];Thaisarco - [Tin] | Compliant
1 | 480-01449-00 | 480-Discrete Semi | DIODE, ARRAY, GP, 1 PAIR SERIES, 75VR, 250mA, SOT23, AMBER | Production | COMP.CAPACITOR | A MCO-006790 | 03/28/2019 04:22:30 AM PDT | 06/19/2019 02:34:10 PM PDT |  | Yes | No |  |  |  |  | AMBER |  |  |  | 480-Discrete Semi | DIODE, ARRAY, GP, 1 PAIR SERIES, 75VR, 250mA, SOT23, AMBER | A MCO-006790 | Production | 10 | Each | 0 | D1A,D2A,D1B,D2B,D1C,D2C,D1D,D2D,D1E,D2E | ORG - AMB |  |  |  |  |  |  |  |  |  |  |  | Central Semiconductor | CMPD6001S TR | DIODE ARRAY GP 75V 250MA SOT23 | non-disti | Active | Preferred |  |  | Missing Info | Malaysia Smelting Corporation (MSC) - [Tin] | Missing Info

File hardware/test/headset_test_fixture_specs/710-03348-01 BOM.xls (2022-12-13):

Level | Part Number | Part Type | Description | Lifecycle Phase | Commodity Code | Rev | Rev Incorp Date | Rev Release Date | Effectivity Date | Shippable Item | Exclude from Rollup | Overall Compliance | Compliance Calculated Date | Mass | Mass-measure | Product Line(s) | Thumbnail | Sites | BOM.Thumbnail | BOM.Item Type | BOM.Item Description | BOM.Item Rev | BOM.Item Lifecycle Phase | BOM.Qty | BOM.UOM | BOM.Find Num | BOM.Ref Des | BOM.Organization | BOM.Usergroup Access - External | BOM.Legacy Item Number | BOM.OK to Purchase | BOM.Substitute | BOM.BOM Notes | BOM.Summary Compliance | BOM.Identifier | BOM.CAD Filename | BOM.Component | BOM.Reference | BOM.Publish Source | Manufacturers.Mfr. Name | Manufacturers.Mfr. Part Number | Manufacturers.Mfr. Part Description | Manufacturers.Mfr Class | Manufacturers.Mfr. Part Lifecycle Phase | Manufacturers.Preferred Status | Manufacturers.Qualification Status | Manufacturers.Reference Notes | Manufacturers.Summary Compliance | Manufacturers.Smelters | Manufacturers.Conflict Mineral Status
0 | 710-03348-01 | 710-EM Assembly | ASSY, ELEC-MECH, TESTER, HEADSET, AMBER | Prototype | ASSY.EM | 01 ECO-033038 | 01/07/2020 02:22:21 PM PST | 01/07/2020 02:22:21 PM PST |  | Yes | No |  |  |  |  | AMBER
1 | 730-05435-01 | 730-Mech Assembly | ASSY, MECH, TESTER, HEADSET, CHASSIS, AMBER | Prototype | ASSY.MECH | 01 ECO-033038 | 01/07/2020 02:22:21 PM PST | 01/07/2020 02:22:21 PM PST |  | Yes | No |  |  |  |  | AMBER |  |  |  | 730-Mech Assembly | ASSY, MECH, TESTER, HEADSET, CHASSIS, AMBER | 01 ECO-033038 | Prototype | 1 | Each | 1 |  | ORG - AMB
2 | 690-15535-01 | 690-Mech Part | MECH, TESTER, HEADSET, CHASSIS, AMBER | Prototype | PART.ME | 01 ECO-033038 | 01/07/2020 02:22:21 PM PST | 01/07/2020 02:22:21 PM PST |  | Yes | No |  |  |  |  | AMBER |  |  |  | 690-Mech Part | MECH, TESTER, HEADSET, CHASSIS, AMBER | 01 ECO-033038 | Prototype | 1 | Each | 1 |  | ORG - AMB
2 | 250-07914-00 | 250-Hardware Part | HW, INSERT, THREADED, HEAT SET, 6-32 UNC-2B, BRASS, AMBER | Production | COMP.HARDWARE | A ECO-033038 | 01/07/2020 02:22:21 PM PST | 01/07/2020 02:22:21 PM PST |  | Yes | No |  |  |  |  | AMBER |  |  |  | 250-Hardware Part | HW, INSERT, THREADED, HEAT SET, 6-32 UNC-2B, BRASS, AMBER | A ECO-033038 | Production | 4 | Each | 2 |  | ORG - AMB |  |  |  |  |  |  |  |  |  |  |  | MCMASTER CARR SUPPLY COMPANY | 94459A290 | HW, INSERT, THREADED, HEAT SET, 6-32 UNC-2B, BRASS | disti | Active | Preferred
2 | 250-07915-00 | 250-Hardware Part | HW, INSERT, HEAT, THREADED, 2-56 UNC-2B, BRASS, AMBER | Production | COMP.HARDWARE | A ECO-033038 | 01/07/2020 02:22:21 PM PST | 01/07/2020 02:22:21 PM PST |  | Yes | No |  |  |  |  | AMBER |  |  |  | 250-Hardware Part | HW, INSERT, HEAT, THREADED, 2-56 UNC-2B, BRASS, AMBER | A ECO-033038 | Production | 12 | Each | 3 |  | ORG - AMB |  |  |  |  |  |  |  |  |  |  |  | MCMASTER CARR SUPPLY COMPANY | 94459A240 | HW, INSERT, HEAT, THREADED, 2-56 UNC-2B, BRASS | disti | Active | Preferred
2 | 250-07721-00 | 250-Hardware Part | HW, BUMPER, THREADED, 6-32 X 1/4IN LG, 1/2IN OD X 1/4IN HGT | Production | COMP.HARDWARE | A ECO-033038 | 01/07/2020 02:22:21 PM PST | 01/07/2020 02:22:21 PM PST |  | Yes | No |  |  |  |  | AMBER |  |  |  | 250-Hardware Part | HW, BUMPER, THREADED, 6-32 X 1/4IN LG, 1/2IN OD X 1/4IN HGT | A ECO-033038 | Production | 4 | Each | 4 |  | ORG - AMB | EXT - All |  |  |  |  |  |  |  |  |  |  | MCMASTER CARR SUPPLY COMPANY | 9541K1 | HW, BUMPER, THREADED, 6-32 X 1/4IN LG, 1/2IN OD X 1/4IN HGT | disti | Active | Preferred
1 | 690-15536-01 | 690-Mech Part | MECH, TESTER, HEADSET, COVER, AMBER | Prototype | PART.ME | 01 ECO-033038 | 01/07/2020 02:22:21 PM PST | 01/07/2020 02:22:21 PM PST |  | Yes | No |  |  |  |  | AMBER |  |  |  | 690-Mech Part | MECH, TESTER, HEADSET, COVER, AMBER | 01 ECO-033038 | Prototype | 1 | Each | 2 |  | ORG - AMB
1 | 650-02729-01 | 650-PCBA | PCBA, HEADSET TESTER BOARD, AMBER | Prototype | ASSY.PCBA | 02 ECO-033518 | 01/07/2020 08:06:28 AM PST | 01/07/2020 08:06:28 AM PST |  | Yes | No |  |  |  |  | AMBER |  |  |  | 650-PCBA | PCBA, HEADSET TESTER BOARD, AMBER | 02 ECO-033518 | Prototype | 1 | Each | 3 |  | ORG - AMB
2 | 150-03883-00 | 150-Capacitor | CAP, CER, NP0, 12PF, 50V, 5%, 0805, AMBER | Production | COMP.CAPACITOR | A MCO-007272 | 04/22/2019 07:26:55 AM PDT | 12/17/2019 06:30:21 PM PST |  | Yes | No |  |  |  |  | AMBER |  |  |  | 150-Capacitor | CAP, CER, NP0, 12PF, 50V, 5%, 0805, AMBER | A MCO-007272 | Production | 2 | Each | 0 | C1,C2 | ORG - AMB |  |  |  |  |  |  |  |  |  |  |  | YAGEO | CC0805JRNPO9BN120 | CAP, CER, NP0, 12PF, 50V, 5%, 0805 | non-disti | Active | Preferred |  |  | Compliant | Malaysia Smelting Corporation (MSC) - [Tin] | Compliant
2 | 150-03884-00 | 150-Capacitor | CAP, CER, X7R, 0.1UF, 25V, 5%, 0805, AMBER | Production | COMP.CAPACITOR | A MCO-007272 | 04/22/2019 07:26:55 AM PDT | 12/17/2019 06:30:21 PM PST |  | Yes | No |  |  |  |  | AMBER |  |  |  | 150-Capacitor | CAP, CER, X7R, 0.1UF, 25V, 5%, 0805, AMBER | A MCO-007272 | Production | 1 | Each | 0 | C3 | ORG - AMB |  |  |  |  |  |  |  |  |  |  |  | AVX | 08053C104JAT2A | CAP, CER, X7R, 0.1UF, 25V, 5%, 0805 | non-disti | Active | Preferred |  |  | Non-Compliant | Malaysia Smelting Corporation (MSC) - [Tin];Aida Chemical Industries Co., Ltd. - [Gold];Allgemeine Gold-und Silberscheideanstalt A.G. - [Gold];AngloGold Ashanti Córrego do Sítio Mineração - [Gold];Argor-Heraeus S.A. - [Gold];Asahi Pretec Corp. - [Gold];Asaka Riken Co., Ltd. - [Gold];PT Bangka Prima Tin - [Tin];PT Sukses Inti Makmur - [Tin];A.L.M.T. TUNGSTEN Corp. - [Tungsten];Kennametal Huntsville - [Tungsten];Chongyi Zhangyuan Tungsten Co., Ltd. - [Tungsten];Aurubis AG - [Gold];Bangko Sentral ng Pilipinas (Central Bank of the Philippines) - [Gold];Boliden AB - [Gold];C. Hafner GmbH + Co. KG - [Gold];CCR Refinery - Glencore Canada Corporation - [Gold];Chimet S.p.A. - [Gold];Dowa - [Gold];Heimerle + Meule GmbH - [Gold];Heraeus Metals Hong Kong Ltd. - [Gold];Heraeus Precious Metals GmbH & Co. KG - [Gold];Ishifuku Metal Industry Co., Ltd. - [Gold];Istanbul Gold Refinery - [Gold];Asahi Refining USA Inc. - [Gold];Asahi Refining Canada Ltd. - [Gold];JX Nippon Mining & Metals Co., Ltd. - [Gold];Kennecott Utah Copper LLC - [Gold];Kojima Chemicals Co., Ltd. - [Gold];LS-NIKKO Copper Inc. - [Gold];Materion - [Gold];Matsuda Sangyo Co., Ltd. - [Gold];Metalor Technologies (Hong Kong) Ltd. - [Gold];Metalor Technologies S.A. - [Gold];Metalor USA Refining Corporation - [Gold];Metalúrgica Met-Mex Peñoles S.A. De C.V. - [Gold];Mitsubishi Materials Corporation - [Gold];Mitsui Mining and Smelting Co., Ltd. - [Gold];Nihon Material Co., Ltd. - [Gold];Elemetal Refining, LLC - [Gold];Ohura Precious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 | Non-Compliant
2 | 150-04316-00 | 150-Capacitor | CAP, CER, X7R, 1µF, 10%, 25V, 0805, AMBER | Production | COMP.CAPACITOR | A MCO-007272 | 11/22/2019 05:23:56 PM PST | 12/17/2019 06:30:21 PM PST |  | Yes | No |  |  |  |  | AMBER |  |  |  | 150-Capacitor | CAP, CER, X7R, 1µF, 10%, 25V, 0805, AMBER | A MCO-007272 | Production | 1 | Each | 0 | C4 | ORG - AMB |  |  |  |  |  |  |  |  |  |  |  | SAMSUNG ELECTRO-MECHANICS | CL21B105KAFNNNE | CAP, CER, X7R, 1µF, 10%, 25V, 0805 | non-disti | Active | Preferred |  |  | Missing Info | Malaysia Smelting Corporation (MSC) - [Tin];PT Timah (Persero) Tbk Kundur - [Tin];PT Timah (Persero) Tbk Mentok - [Tin];Thaisarco - [Tin] | Missing Info
2 | 150-04317-00 | 150-Capacitor | CAP, CER, X5R, 4.7UF, 10%, 10V, 0805, AMBER | Production | COMP.CAPACITOR | A MCO-007272 | 11/22/2019 05:23:56 PM PST | 12/17/2019 06:30:21 PM PST |  | Yes | No |  |  |  |  | AMBER |  |  |  | 150-Capacitor | CAP, CER, X5R, 4.7UF, 10%, 10V, 0805, AMBER | A MCO-007272 | Production | 1 | Each | 0 | C5 | ORG - AMB |  |  |  |  |  |  |  |  |  |  |  | MURATA | GRM219R61A475KE34D | CAP, CER, X5R, 4.7µF, 10%, 10V, 0805 | non-disti | Active | Preferred |  |  | Non-Compliant | H.C. Starck GmbH Goslar - [Tantalum];Mitsui Mining and Smelting Co., Ltd. - [Tantalum];Taki Chemical Co., Ltd. - [Tantalum];Jiujiang Tanbre Co., Ltd. - [Tantalum];Conghua Tantalum and Niobium Smeltry - [Tantalum];Ningxia Orient Tantalum Industry Co., Ltd. - [Tantalum];Global Advanced Metals Boyertown - [Tantalum];F&X Electro-Materials Ltd. - [Tantalum];H.C. Starck Inc. - [Tantalum];Mitsubishi Materials Corporation - [Tin];Thaisarco - [Tin];PT Timah (Persero) Tbk Mentok - [Tin];Minsur - [Tin];CV United Smelting - [Tin];PT Bukit Timah - [Tin];Malaysia Smelting Corporation (MSC) - [Tin];EM Vinto - [Tin];Metallo-Chimique N.V. - [Tin];Mineração Taboca S.A. - [Tin];Operaciones Metalurgical S.A. - [Tin];Yunnan Tin Company Limited - [Tin];PT Timah (Persero) Tbk Kundur - [Tin];Gejiu Non-Ferrous Metal Processing Co., Ltd. - [Tin];PT Refined Bangka Tin - [Tin];PT Stanindo Inti Perkasa - [Tin];Cooperativa Metalurgica de Rondônia Ltda. - [Tin];Alpha - [Tin];Tanaka Kikinzoku Kogyo K.K. - [Gold];Mitsubishi Materials Corporation - [Gold];Asahi Refining USA Inc. - [Gold];Matsuda Sangyo Co., Ltd. - [Gold];Nihon Material Co., Ltd. - [Gold];Asahi Pretec Corp. - [Gold];Heraeus Metals Hong Kong Ltd. - [Gold];Eco-System Recycling Co., Ltd. - [Gold];Ishifuku Metal Industry Co., Ltd. - [Gold];JX Nippon Mining & Metals Co., Ltd. - [Gold];Mitsui Mining and Smelting Co., Ltd. - [Gold];Sumitomo Metal Mining Co., Ltd. - [Gold];Dowa - [Gold];Western Australian Mint trading as The Perth Mint - [Gold];Meta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 | Non-Compliant
2 | 210-04187-00 | 210-Connector | CONN, HDR, VERT, 1x3, 2.54MM P, 2.54MM H, GOLD, TH, AMBER | Production | COMP.CONNECTOR | A MCO-007272 | 04/22/2019 07:26:55 AM PDT | 12/17/2019 06:30:21 PM PST |  | Yes | No |  |  |  |  | AMBER |  |  |  | 210-Connector | CONN, HDR, VERT, 1x3, 2.54MM P, 2.54MM H, GOLD, TH, AMBER | A MCO-007272 | Production | 4 | Each | 0 | J3,J4,J5,J6 | ORG - AMB |  |  |  |  |  |  |  |  |  |  |  | HARWIN INC | M20-9990345 | CONN, HDR, VERT, 1x3, 2.54MM P, 2.54MM H, GOLD, TH | non-disti | Active | Preferred |  |  | Missing Info | Aida Chemical Industries Co., Ltd. - [Gold];Allgemeine Gold-und Silberscheideanstalt A.G. - [Gold];AngloGold Ashanti Córrego do Sítio Mineração - [Gold];Argor-Heraeus S.A. - [Gold];Asahi Pretec Corp. - [Gold];Asaka Riken Co., Ltd. - [Gold];PT Bangka Prima Tin - [Tin];PT Sukses Inti Makmur - [Tin];A.L.M.T. TUNGSTEN Corp. - [Tungsten];Kennametal Huntsville - [Tungsten];Chongyi Zhangyuan Tungsten Co., Ltd. - [Tungsten];Aurubis AG - [Gold];Bangko Sentral ng Pilipinas (Central Bank of the Philippines) - [Gold];Boliden AB - [Gold];C. Hafner GmbH + Co. KG - [Gold];CCR Refinery - Glencore Canada Corporation - [Gold];Chimet S.p.A. - [Gold];Dowa - [Gold];Heimerle + Meule GmbH - [Gold];Heraeus Metals Hong Kong Ltd. - [Gold];Heraeus Precious Metals GmbH & Co. KG - [Gold];Ishifuku Metal Industry Co., Ltd. - [Gold];Istanbul Gold Refinery - [Gold];Asahi Refining USA Inc. - [Gold];Asahi Refining Canada Ltd. - [Gold];JX Nippon Mining & Metals Co., Ltd. - [Gold];Kennecott Utah Copper LLC - [Gold];Kojima Chemicals Co., Ltd. - [Gold];LS-NIKKO Copper Inc. - [Gold];Materion - [Gold];Matsuda Sangyo Co., Ltd. - [Gold];Metalor Technologies (Hong Kong) Ltd. - [Gold];Metalor Technologies S.A. - [Gold];Metalor USA Refining Corporation - [Gold];Metalúrgica Met-Mex Peñoles S.A. De C.V. - [Gold];Mitsubishi Materials Corporation - [Gold];Mitsui Mining and Smelting Co., Ltd. - [Gold];Nihon Material Co., Ltd. - [Gold];Elemetal Refining, LLC - [Gold];Ohura Precious Metal Industry Co., Ltd. - [Gold];PAMP S.A.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 | Missing Info
2 | 210-04464-00 | 210-Connector | CONN, HDR, TH, STR, 1X6, 2.5MM P, 5.9mm H, TIN, AMBER | Production | COMP.CONNECTOR | A MCO-007272 | 11/22/2019 05:23:56 PM PST | 12/17/2019 06:30:21 PM PST |  | Yes | No |  |  |  |  | AMBER |  |  |  | 210-Connector | CONN, HDR, TH, STR, 1X6, 2.5MM P, 5.9mm H, TIN, AMBER | A MCO-007272 | Production | 1 | Each | 0 | J1 | ORG - AMB |  |  |  |  |  |  |  |  |  |  |  | MOLEX | 22-03-5065 | CONN, HDR, TH, STR, 1X6, 2.5MM P, 5.9mm H, TIN | non-disti | Active | Preferred |  |  | Non-Compliant | CV United Smelting - [Tin];Dowa - [Tin];Ganzhou Seadragon W & Mo Co., Ltd. - [Tungsten];Chenzhou Diamond Tungsten Products Co., Ltd. - [Tungsten];H.C. Starck GmbH - [Tungsten];H.C. Starck Smelting GmbH & Co.KG - [Tungsten];Nui Phao H.C. Starck Tungsten Chemicals Manufacturing LLC - [Tungsten];Jiangwu H.C. Starck Tungsten Products Co., Ltd. - [Tungsten];Hunan Chuangda Vanadium Tungsten Co., Ltd. Wuji - [Tungsten];Hydrometallurg, JSC - [Tungsten];Advanced Chemical Company - [Gold];Aida Chemical Industries Co., Ltd. - [Gold];Allgemeine Gold-und Silberscheideanstalt A.G. - [Gold];Almalyk Mining and Metallurgical Complex (AMMC) - [Gold];AngloGold Ashanti Córrego do Sítio Mineração - [Gold];Argor-Heraeus S.A. - [Gold];Asahi Pretec Corp. - [Gold];Asaka Riken Co., Ltd. - [Gold];Atasay Kuyumculuk Sanayi Ve Ticaret A.S. - [Gold];Aurubis AG - [Gold];Bangko Sentral ng Pilipinas (Central Bank of the Philippines) - [Gold];Boliden AB - [Gold];C. Hafner GmbH + Co. KG - [Gold];VQB Mineral and Trading Group JSC - [Tin];White Solder Metalurgia e Mineração Ltda. - [Tin];Yunnan Chengfeng Non-ferrous Metals Co., Ltd. - [Tin];Magnu's Minerais Metais e Ligas Ltda. - [Tin];PT Wahana Perkit Jaya - [Tin];Melt Metais e Ligas S.A. - [Tin];PT ATD Makmur Mandiri Jaya - [Tin];Phoenix Metal Ltd. - [Tin];O.M. Manufacturing Philippines, Inc. - [Tin];PT Inti Stania Prima - [Tin];An Vinh Joint Stock Mineral Processing Company - [Tin];Metallo-Chimique N.V. - [Tin];Elmet S.L.U. - [Tin];Kennametal Huntsville - [T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 | Non-Compliant
2 | 210-04466-00 | 210-Connector | CONN, SKT, USB 2, TYPE B, RA, 4 PIN, 2.5mmP, GOLD, TH, 11.15mm, AMBER | Production | COMP.CONNECTOR | A MCO-007272 | 11/22/2019 05:23:56 PM PST | 12/17/2019 06:30:21 PM PST |  | Yes | No |  |  |  |  | AMBER |  |  |  | 210-Connector | CONN, SKT, USB 2, TYPE B, RA, 4 PIN, 2.5mmP, GOLD, TH, 11.15mm, AMBER | A MCO-007272 | Production | 1 | Each | 0 | J8 | ORG - AMB |  |  |  |  |  |  |  |  |  |  |  | TE CONNECTIVITY | 292304-1 | CONN, SKT, USB 2, TYPE B, RA, 4 PIN, 2.5mmP, GOLD, TH, 11.15mm | non-disti | Active | Preferred |  |  | Missing Info
2 | 230-00419-00 | 230-Crystal/Osc | CRYSTAL, 32.768KHZ, 20PPM, 12.5PF, 35 KOHM ESR, RADIAL, CAN, AMBER | Production | COMP.CRYSTAL-OSC | A MCO-007272 | 04/22/2019 07:26:55 AM PDT | 12/17/2019 06:30:21 PM PST |  | Yes | No |  |  |  |  | AMBER |  |  |  | 230-Crystal/Osc | CRYSTAL, 32.768KHZ, 20PPM, 12.5PF, 35 KOHM ESR, RADIAL, CAN, AMBER | A MCO-007272 | Production | 1 | Each | 0 | Y1 | ORG - AMB |  |  |  |  |  |  |  |  |  |  |  | Citizen Electronics Co. | CFS-20632768DZFB | CRYSTAL, 32.768KHZ, 20PPM, 12.5PF, 35 KOHM ESR, RADIAL, CAN | non-disti | Active | Preferred |  |  | Missing Info | Aurubis AG - [Gold];BANGALORE REFINERY - [GOLD];Bangko Sentral ng Pilipinas (Central Bank of the Philippines) - [Gold];Boliden AB - [Gold];C. Hafner GmbH + Co. KG - [Gold];Caridad - [Gold];CCR Refinery - Glencore Canada Corporation - [Gold];Cendres + Métaux S.A. - [Gold];Chimet S.p.A. - [Gold];Chugai Mining - [Gold];Daejin Indus Co., Ltd. - [Gold];Daye Non-Ferrous Metals Mining Ltd. - [Gold];DODUCO GmbH - [Gold];Dowa - [Gold];DSC (Do Sung Corporation) - [Gold];Eco-System Recycling Co., Ltd. - [Gold];Elemetal Refining, LLC - [Gold];Emirates Gold DMCC - [Gold];Gansu Seemine Material Hi-Tech Co., Ltd. - [Gold];Geib Refining Corporation - [Gold];Great Wall Precious Metals Co., LTD. of CBPM - [Gold];Guangdong Jinding Gold Limited - [Gold];GUJARAT GOLD CENTRE - [GOLD];Guoda Safina High-Tech Environmental Refinery Co., Ltd. - [Gold];Hangzhou Fuchunjiang Smelting Co., Ltd. - [Gold];Heimerle + Meule GmbH - [Gold];Heraeus Metals Hong Kong Ltd. - [Gold];Heraeus Precious Metals GmbH & Co. KG - [Gold];Hunan Chenzhou Mining Co., Ltd. - [Gold];HwaSeong CJ CO., LTD. - [Gold];Jiangxi Copper Co., Ltd. - [Gold];JSC Ekaterinburg Non-Ferrous Metal Processing Plant - [Gold];JSC Uralelectromed - [Gold];JX Nippon Mining & Metals Co., Ltd. - [Gold];Kaloti Precious Metals - [Gold];Kazakhmys Smelting LLC - [Gold];Kazzinc - [Gold];Kennecott Utah Copper LLC - [Gold];KGHM Polska Mied? Spó?ka Akcyjna - [Gold];Inner Mongolia Qiankun Gold and Silver Refinery Share Co., Ltd. - [Gold];Ishifuku Metal Industry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 | Missing Info
2 | 250-07858-00 | 250-Hardware Part | HW, SNAP, STUD, 3.2mm LG, OD 7.5mm, .130 SERIES, BRASS, AMBER | Production | COMP.HARDWARE | A ECO-033518 | 01/07/2020 08:06:28 AM PST | 01/07/2020 08:06:28 AM PST |  | Yes | No |  |  |  |  | AMBER |  |  |  | 250-Hardware Part | HW, SNAP, STUD, 3.2mm LG, OD 7.5mm, .130 SERIES, BRASS, AMBER | A ECO-033518 | Production | 2 | Each | 0 | MH5,MH6 | ORG - AMB |  |  |  |  |  |  |  |  |  |  |  | Rome Fastener Corporation | 76 STUD | HW, SNAP, STUD, 3.2mm LG, OD 7.5mm, .130 SERIES, BRASS | disti | Active | Preferred
2 | 250-07859-00 | 250-Hardware Part | HW, SNAP, STUD, 0.128 in LG, 0.490in OD, BRASS, AMBER | Production | COMP.HARDWARE | A ECO-033518 | 01/07/2020 08:06:28 AM PST | 01/07/2020 08:06:28 AM PST |  | Yes | No |  |  |  |  | AMBER |  |  |  | 250-Hardware Part | HW, SNAP, STUD, 0.128 in LG, 0.490in OD, BRASS, AMBER | A ECO-033518 | Production | 4 | Each | 0 | MH1,MH2,MH3,MH4 | ORG - AMB |  |  |  |  |  |  |  |  |  |  |  | Rome Fastener Corporation | 91 STUD | HW, SNAP, STUD, 0.128 in LG, 0.490in OD, BRASS | disti | Active | Preferred
2 | 313-05199-00 | 313-IC | IC, BINARY COUNTER, CD4060B, 1 ELEMENT, 14-BIT, 3 TO 18 VIN, TSSOP-16, AMBER | Production | COMP.IC | A MCO-007272 | 04/22/2019 07:26:55 AM PDT | 12/17/2019 06:30:21 PM PST |  | Yes | No |  |  |  |  | AMBER |  |  |  | 313-IC | IC, BINARY COUNTER, CD4060B, 1 ELEMENT, 14-BIT, 3 TO 18 VIN, TSSOP-16, AMBER | A MCO-007272 | Production | 1 | Each | 0 | U1 | ORG - AMB |  |  |  |  |  |  |  |  |  |  |  | TEXAS INSTRUMENTS INC | CD4060BPWR | IC, BINARY COUNTER, CD4060B, 1 ELEMENT, 14-BIT, 3 TO 18 VIN, TSSOP-16 | non-disti | Active | Preferred |  |  | Non-Compliant | Aurubis AG - [Gold];Bangko Sentral ng Pilipinas (Central Bank of the Philippines) - [Gold];Boliden AB - [Gold];C. Hafner GmbH + Co. KG - [Gold];CCR Refinery - Glencore Canada Corporation - [Gold];Chimet S.p.A. - [Gold];Dowa - [Gold];Elemetal Refining, LLC - [Gold];Heimerle + Meule GmbH - [Gold];Heraeus Metals Hong Kong Ltd. - [Gold];Heraeus Precious Metals GmbH & Co. KG - [Gold];JX Nippon Mining & Metals Co., Ltd. - [Gold];Kennecott Utah Copper LLC - [Gold];Ishifuku Metal Industry Co., Ltd. - [Gold];Istanbul Gold Refinery - [Gold];Kojima Chemicals Co., Ltd. - [Gold];LS-NIKKO Copper Inc. - [Gold];Materion - [Gold];Matsuda Sangyo Co., Ltd. - [Gold];Metalor Technologies (Hong Kong) Ltd. - [Gold];Metalor Technologies S.A. - [Gold];Metalor USA Refining Corporation - [Gold];Metalúrgica Met-Mex Peñoles S.A. De C.V. - [Gold];Mitsubishi Materials Corporation - [Gold];Mitsui Mining and Smelting Co., Ltd. - [Gold];Nihon Material Co., Ltd. - [Gold];Ohura Precious Metal Industry Co., Ltd. - [Gold];PAMP S.A. - [Gold];Republic Metals Corporation - [Gold];Royal Canadian Mint - [Gold];SEMPSA Joyería Platería S.A. - [Gold];Shandong Zhaojin Gold & Silver Refinery Co., Ltd. - [Gold];Solar Applied Materials Technology Corp. - [Gold];Sumitomo Metal Mining Co., Ltd. - [Gold];Tanaka Kikinzoku Kogyo K.K. - [Gold];Tokuriki Honten Co., Ltd. - [Gold];Umicore Precious Metals Thailand - [Gold];Umicore SA Business Unit Precious Metals Refining - [Gold];United Precious Metal Refining, Inc. - [Gold];Wester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 | Non-Compliant
2 | 313-05482-00 | 313-IC | IC, REG, LINEAR, TPS769XX, 100mA, 10VIN, 2.5VOUT, SOT-23-5, AMBER | Production | COMP.IC | A MCO-007272 | 11/22/2019 05:23:56 PM PST | 12/17/2019 06:30:21 PM PST |  | Yes | No |  |  |  |  | AMBER |  |  |  | 313-IC | IC, REG, LINEAR, TPS769XX, 100mA, 10VIN, 2.5VOUT, SOT-23-5, AMBER | A MCO-007272 | Production | 1 | Each | 0 | U2 | ORG - AMB |  |  |  |  |  |  |  |  |  |  |  | TEXAS INSTRUMENTS INC | TPS76925DBVR | IC, REG, LINEAR, TPS769XX, 100mA, 10VIN, 2.5VOUT, SOT-23-5 | non-disti | Active | Preferred |  |  | Non-Compliant | Aurubis AG - [Gold];BANGALORE REFINERY - [GOLD];Bangko Sentral ng Pilipinas (Central Bank of the Philippines) - [Gold];Boliden AB - [Gold];C. Hafner GmbH + Co. KG - [Gold];Caridad - [Gold];CCR Refinery - Glencore Canada Corporation - [Gold];Cendres + Métaux S.A. - [Gold];Chimet S.p.A. - [Gold];Chugai Mining - [Gold];Daejin Indus Co., Ltd. - [Gold];Daye Non-Ferrous Metals Mining Ltd. - [Gold];DODUCO GmbH - [Gold];Dowa - [Gold];DSC (Do Sung Corporation) - [Gold];Eco-System Recycling Co., Ltd. - [Gold];Elemetal Refining, LLC - [Gold];Emirates Gold DMCC - [Gold];Gansu Seemine Material Hi-Tech Co., Ltd. - [Gold];Geib Refining Corporation - [Gold];Great Wall Precious Metals Co., LTD. of CBPM - [Gold];Guangdong Jinding Gold Limited - [Gold];GUJARAT GOLD CENTRE - [GOLD];Guoda Safina High-Tech Environmental Refinery Co., Ltd. - [Gold];Hangzhou Fuchunjiang Smelting Co., Ltd. - [Gold];Heimerle + Meule GmbH - [Gold];Heraeus Metals Hong Kong Ltd. - [Gold];Heraeus Precious Metals GmbH & Co. KG - [Gold];Hunan Chenzhou Mining Co., Ltd. - [Gold];HwaSeong CJ CO., LTD. - [Gold];Jiangxi Copper Co., Ltd. - [Gold];JSC Ekaterinburg Non-Ferrous Metal Processing Plant - [Gold];JSC Uralelectromed - [Gold];JX Nippon Mining & Metals Co., Ltd. - [Gold];Kaloti Precious Metals - [Gold];Kazakhmys Smelting LLC - [Gold];Kazzinc - [Gold];Kennecott Utah Copper LLC - [Gold];KGHM Polska Mied? Spó?ka Akcyjna - [Gold];Inner Mongolia Qiankun Gold and Silver Refinery Share Co., Ltd. - [Gold];Ishifuku Metal Industry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 | Non-Compliant
2 | 470-16962-00 | 470-Resistor | RES, 10M, 5%, 1/8W, 0805, AUTOGRADE, AMBER | Production | COMP.RESISTOR | A MCO-007272 | 04/22/2019 07:26:55 AM PDT | 12/17/2019 06:30:21 PM PST |  | Yes | No |  |  |  |  | AMBER |  |  |  | 470-Resistor | RES, 10M, 5%, 1/8W, 0805, AUTOGRADE, AMBER | A MCO-007272 | Production | 5 | Each | 0 | R1,R3,R4,R5,R6 | ORG - AMB |  |  |  |  |  |  |  |  |  |  |  | PANASONIC | ERJ-6GEYJ106V | RES, 10M, 5%, 1/8W, 0805, AUTOGRADE | non-disti | Active | Preferred |  |  | Missing Info | Aida Chemical Industries Co., Ltd. - [Gold];Allgemeine Gold-und Silberscheideanstalt A.G. - [Gold];AngloGold Ashanti Córrego do Sítio Mineração - [Gold];Argor-Heraeus S.A. - [Gold];Asahi Pretec Corp. - [Gold];Asaka Riken Co., Ltd. - [Gold];PT Bangka Prima Tin - [Tin];PT Sukses Inti Makmur - [Tin];A.L.M.T. TUNGSTEN Corp. - [Tungsten];Kennametal Huntsville - [Tungsten];Chongyi Zhangyuan Tungsten Co., Ltd. - [Tungsten];Aurubis AG - [Gold];Bangko Sentral ng Pilipinas (Central Bank of the Philippines) - [Gold];Boliden AB - [Gold];C. Hafner GmbH + Co. KG - [Gold];CCR Refinery - Glencore Canada Corporation - [Gold];Chimet S.p.A. - [Gold];Dowa - [Gold];Heimerle + Meule GmbH - [Gold];Heraeus Metals Hong Kong Ltd. - [Gold];Heraeus Precious Metals GmbH & Co. KG - [Gold];Ishifuku Metal Industry Co., Ltd. - [Gold];Istanbul Gold Refinery - [Gold];Asahi Refining USA Inc. - [Gold];Asahi Refining Canada Ltd. - [Gold];JX Nippon Mining & Metals Co., Ltd. - [Gold];Kennecott Utah Copper LLC - [Gold];Kojima Chemicals Co., Ltd. - [Gold];LS-NIKKO Copper Inc. - [Gold];Materion - [Gold];Matsuda Sangyo Co., Ltd. - [Gold];Metalor Technologies (Hong Kong) Ltd. - [Gold];Metalor Technologies S.A. - [Gold];Metalor USA Refining Corporation - [Gold];Metalúrgica Met-Mex Peñoles S.A. De C.V. - [Gold];Mitsubishi Materials Corporation - [Gold];Mitsui Mining and Smelting Co., Ltd. - [Gold];Nihon Material Co., Ltd. - [Gold];Elemetal Refining, LLC - [Gold];Ohura Precious Metal Industry Co., Ltd. - [Gold];PAMP S.A.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 | Missing Info
2 | 470-16963-00 | 470-Resistor | RES, 330K, 0.1%, 1/8W, 0805, AUTOGRADE, AMBER | Production | COMP.RESISTOR | A MCO-007272 | 04/22/2019 07:26:55 AM PDT | 12/17/2019 06:30:21 PM PST |  | Yes | No |  |  |  |  | AMBER |  |  |  | 470-Resistor | RES, 330K, 0.1%, 1/8W, 0805, AUTOGRADE, AMBER | A MCO-007272 | Production | 1 | Each | 0 | R2 | ORG - AMB |  |  |  |  |  |  |  |  |  |  |  | PANASONIC | ERA-6AEB334V | RES, 330K, 0.1%, 1/8W, 0805, AUTOGRADE | non-disti | Active | Preferred |  |  | Missing Info | Tanaka Kikinzoku Kogyo K.K. - [Gold];Tokuriki Honten Co., Ltd. - [Gold];Umicore SA Business Unit Precious Metals Refining - [Gold];United Precious Metal Refining, Inc. - [Gold];Western Australian Mint trading as The Perth Mint - [Gold];Zhongyuan Gold Smelter of Zhongjin Gold Corporation - [Gold];Umicore Precious Metals Thailand - [Gold];Republic Metals Corporation - [Gold];Ögussa Österreichische Gold- und Silber-Scheideanstalt GmbH - [Gold];Changsha South Tantalum Niobium Co., Ltd. - [Tantalum];Conghua Tantalum and Niobium Smeltry - [Tantalum];Duoluoshan - [Tantalum];Exotech Inc. - [Tantalum];F&X Electro-Materials Ltd. - [Tantalum];JiuJiang JinXin Nonferrous Metals Co., Ltd. - [Tantalum];LSM Brasil S.A. - [Tantalum];Mineração Taboca S.A. - [Tantalum];Ningxia Orient Tantalum Industry Co., Ltd. - [Tantalum];Ulba Metallurgical Plant JSC - [Tantalum];Zhuzhou Cemented Carbide Group Co., Ltd. - [Tantalum];Hengyang King Xing Lifeng New Materials Co., Ltd. - [Tantalum];D Block Metals, LLC - [Tantalum];Plansee SE Liezen - [Tantalum];H.C. Starck Co., Ltd. - [Tantalum];H.C. Starck GmbH Goslar - [Tantalum];H.C. Starck GmbH Laufenburg - [Tantalum];H.C. Starck Hermsdorf GmbH - [Tantalum];H.C. Starck Inc. - [Tantalum];H.C. Starck Ltd. - [Tantalum];H.C. Starck Smelting GmbH & Co. KG - [Tantalum];Plansee SE Reutte - [Tantalum];Global Advanced Metals Boyertown - [Tantalum];Global Advanced Metals Aizu - [Tantalum];Jiangxi Ketai Advanced Material Co., Ltd. - [Tin];Alpha - [Tin];Cooperativa Met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 | Missing Info
2 | 470-17255-00 | 470-Resistor | RES, 1K, 1%, 1/8W, 0805, AMBER | Production | COMP.RESISTOR | A MCO-007272 | 11/22/2019 05:23:56 PM PST | 12/17/2019 06:30:21 PM PST |  | Yes | No |  |  |  |  | AMBER |  |  |  | 470-Resistor | RES, 1K, 1%, 1/8W, 0805, AMBER | A MCO-007272 | Production | 4 | Each | 0 | R7,R8,R9,R10 | ORG - AMB |  |  |  |  |  |  |  |  |  |  |  | VISHAY | CRCW08051K00FKEAC | RES, 1K, 1%, 1/8W, 0805 | non-disti | Active | Preferred |  |  | Non-Compliant | F&X Electro-Materials Ltd. - [Tantalum];Exotech Inc. - [Tantalum];Duoluoshan - [Tantalum];Conghua Tantalum and Niobium Smeltry - [Tantalum];PT Cipta Persada Mulia - [Tin];PT Inti Stania Prima - [Tin];Changsha South Tantalum Niobium Co., Ltd. - [Tantalum];Global Advanced Metals Aizu - [Tantalum];Global Advanced Metals Boyertown - [Tantalum];Plansee SE Reutte - [Tantalum];H.C. Starck Smelting GmbH & Co. KG - [Tantalum];H.C. Starck Ltd. - [Tantalum];H.C. Starck Inc. - [Tantalum];H.C. Starck Hermsdorf GmbH - [Tantalum];H.C. Starck GmbH Laufenburg - [Tantalum];H.C. Starck GmbH Goslar - [Tantalum];H.C. Starck Co., Ltd. - [Tantalum];Plansee SE Liezen - [Tantalum];Zhuzhou Cemented Carbide Group Co., Ltd. - [Tantalum];Yichun Jin Yang Rare Metal Co., Ltd. - [Tantalum];Ulba Metallurgical Plant JSC - [Tantalum];Taki Chemical Co., Ltd. - [Tantalum];Solikamsk Magnesium Works OAO - [Tantalum];Ningxia Orient Tantalum Industry Co., Ltd. - [Tantalum];Mitsui Mining & Smelting - [Tantalum];Mineração Taboca S.A. - [Tantalum];LSM Brasil S.A. - [Tantalum];Jiujiang Tanbre Co., Ltd. - [Tantalum];JiuJiang JinXin Nonferrous Metals Co., Ltd. - [Tantalum];Hengyang King Xing Lifeng New Materials Co., Ltd. - [Tantalum];Guangdong Zhiyuan New Material Co., Ltd. - [Tantalum];O.M. Manufacturing Philippines, Inc. - [Tin];Phoenix Metal Ltd. - [Tin];PT Wahana Perkit Jaya - [Tin];PT ATD Makmur Mandiri Jaya - [Tin];VQB Mineral and Trading Group JSC - [Tin];Metallic Resources, Inc. - [Tin];Dowa - [Tin];PT Panca Me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 | Non-Compliant
2 | 651-02729-01 | 651-PCB | PCB, HEADSET TESTER BOARD, AMBER | Prototype | PART.PCB | 01 MCO-007273 | 12/17/2019 06:09:15 PM PST | 01/06/2020 06:40:12 PM PST |  | Yes | No |  |  |  |  | AMBER |  |  |  | 651-PCB | PCB, HEADSET TESTER BOARD, AMBER | 01 MCO-007273 | Prototype | 1 | Each | 0 | PCB1 | ORG - AMB
1 | 250-07916-00 | 250-Hardware Part | HW, SCREW, PHH FLH, NO. 6, THD FORM, ZINC PLD STL, AMBER | Production | COMP.HARDWARE | A ECO-033038 | 01/07/2020 02:22:21 PM PST | 01/07/2020 02:22:21 PM PST |  | Yes | No |  |  |  |  | AMBER |  |  |  | 250-Hardware Part | HW, SCREW, PHH FLH, NO. 6, THD FORM, ZINC PLD STL, AMBER | A ECO-033038 | Production | 8 | Each | 4 |  | ORG - AMB |  |  |  |  |  |  |  |  |  |  |  | MCMASTER CARR SUPPLY COMPANY | 90048A148 | HW, SCREW, PHH FLH, NO. 6, THD FORM, ZINC PLD STL | disti | Active | Preferred
1 | 250-07917-00 | 250-Hardware Part | HW, SCREW, PHH FLH, M3 x 0.5 x 10mm LG, ZINC PLD STL, AMBER | Production | COMP.HARDWARE | A ECO-033038 | 01/07/2020 02:22:21 PM PST | 01/07/2020 02:22:21 PM PST |  | Yes | No |  |  |  |  | AMBER |  |  |  | 250-Hardware Part | HW, SCREW, PHH FLH, M3 x 0.5 x 10mm LG, ZINC PLD STL, AMBER | A ECO-033038 | Production | 2 | Each | 5 |  | ORG - AMB |  |  |  |  |  |  |  |  |  |  |  | MCMASTER CARR SUPPLY COMPANY | 91420A120 | HW, SCREW, PHH FLH, M3 x 0.35 x 0.5 x 10mm LG, SCZ | disti | Active | Preferred |  |  | Missing Info
1 | 250-07918-00 | 250-Hardware Part | HW, SCREW, FLH PHH, 2-56 UNC-2A, ZINC PL STL, AMBER | Production | COMP.HARDWARE | A ECO-033038 | 01/07/2020 02:22:21 PM PST | 01/07/2020 02:22:21 PM PST |  | Yes | No |  |  |  |  | AMBER |  |  |  | 250-Hardware Part | HW, SCREW, FLH PHH, 2-56 UNC-2A, ZINC PL STL, AMBER | A ECO-033038 | Production | 12 | Each | 6 |  | ORG - AMB |  |  |  |  |  |  |  |  |  |  |  | MCMASTER CARR SUPPLY COMPANY | 90273A050 | HW, SCREW, FLH PHH, 2-56 UNC-2A, ZINC PL STL | disti | Active | Preferred

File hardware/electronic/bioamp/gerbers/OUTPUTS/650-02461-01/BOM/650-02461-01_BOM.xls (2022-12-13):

Fitted | Designator | Description1 | Manufacturer Part Number | Quantity
Fitted | C1A, C1B, C1C, C1D, C2A, C2B, C2C, C2D, C51, C52 | Cap Ceramic Array 0.0047uF 50V X7R 20% 1206 SMD 4 Capacitor 125C Plastic T/R | CKCA43X7R1H472M100AA | 10
Fitted | C3A, C3B, C3C, C3D, C20A, C20B, C20C, C20D, C21A, C21B, C21C, C21D, C94, C97, C102 | 10µF ±20% 6.3V X7R Ceramic Capacitor -55°C ~ 125°C Surface Mount, MLCC 0603 (1608 Metric) 0.063" L x 0.031" W (1.60mm x 0.80mm) | CL10B106MQ8NRNC | 15
Fitted | C4A, C4B, C4C, C4D, C6A, C6B, C6C, C6D, C8A, C8B, C8C, C8D, C11A, C11B, C11C, C11D, C14A, C14B, C14C, C14D, C96, C99, C100, C101 | AVX 0402YD104KAT2A Multilayer Ceramic Capacitor, 0.1 F, 10%, X5R, 16 V, 0402 [1005 Metric] | 0402YD104KAT2A | 24
Fitted | C5A, C5B, C5C, C5D, C7A, C7B, C7C, C7D, C10A, C10B, C10C, C10D, C12A, C12B, C12C, C12D, C13A, C13B, C13C, C13D, C47, C49, C54A, C54B, C55A, C55B, C56A, C56B, C57A, C57B, C58A, C58B, C61, C67, C70, C72, C73, C75, C76, C77, C78, C95, C98 | 1µF ±10% 16V JB Ceramic Capacitor -25°C ~ 85°C Surface Mount, MLCC 0402 (1005 Metric) 0.039" L x 0.020" W (1.00mm x 0.50mm) | CGB2A1JB1C105K033BC | 43
Fitted | C9A, C9B, C9C, C9D | CAP TANT POLY 100UF 4V 1411 | T520T107M004ATE070 | 4
Fitted | C15, C53 | CAP CER 4700PF 50V X7R 0402 | GCM155R71H472KA37D | 2
Fitted | C16, C17, C19 | Cap Tant Organic 150uF 10VDC D CASE 20% (7.3 X 4.3 X 2.8mm) SMD 7343-31 0.005 Ohm 125C T/R | T530D157M010ATE005 | 3
Fitted | C18, C59, C60, C62, C63, C68, C69 | MURATA GRM31CR71C106KA12L SMD Multilayer Ceramic Capacitor, 10 F, 10%, X7R, 16 V, 1206 [3216 Metric] | GRM31CR71C106KA12L | 7
Fitted | C48, C50 | Multilayer Ceramic Capacitors MLCC - SMD/SMT 16volts 0.01uF 10% | 520L103KT16T | 2
Fitted | C71, C74 | Cap Ceramic 2.2uF 16V X5R 10% SMD 0402 85C Cardboard T/R | CL05A225KO5NQNC | 2
Fitted | D1A, D1B, D1C, D1D, D8A, D8B, D9A, D9B, D12, D13, D14, D15, D16, D31 | Standard LEDs - SMD 0402 SOFT ORANGE Non-Diff | VLMO1500-GS08 | 14
Fitted | D2 | BROADCOM LIMITED ASMB-TTB0-0A3A2 LED, RGB, Red, Green, Blue, R 790mcd, G 2.4cd, B 500mcd, 115 , R 2.1V, G 3.1V, B 3.1V | ASMB-TTB0-0A3A2 | 1
Fitted | D6, D7, D20 |  | TPD1E0B04DPYR | 3
Fitted | D10, D11, D18, D19 | DIODE SCHOTTKY 40V 3A SMA | B340A-13-F | 4
Fitted | J1 |  | S8211-46R | 1
Fitted | J3 |  | 5749070-7 | 1
Fitted | J5, J6 | CONN RECPT RUGGED USB B IP67 | MUSBD111M0 | 2
Fitted | J9 | Conn Micro SD Card SKT 8 POS 1.1mm Solder RA SMD 0.5A/Contact Embossed T/R | 503398-1892 | 1
Fitted | JP1, JP2, JP3 | Headers & Wire Housings WR-PHD 2.54mm Header 2P THT | 61300211121 | 3
Fitted | JP4, JP5 | CONN JUMPER SHORTING .100" GOLD | QPC02SXGN-RC | 2
Fitted | OP1A, OP1B, OP2A, OP2B | OPTOISO 5KV PUSH PULL 6SO | ACPL-W61L-560E | 4
Fitted | PS1 | CONVERTER DC/DC 5V OUT 1W | VHS1-S5-S5-SIP | 1
Fitted | R1A, R1B, R1C, R1D, R38 | Res Thick Film Array 4.7K Ohm 5% 1/4W ±200ppm/°C ISOL 16-Pin 1506(8 X 0402) Convex SMD Punched Carrier T/R | EXB-2HV472JV | 5
Fitted | R2A, R2B, R2C, R2D, R5, R6, R7, R42A, R42B, R43A, R43B, R57, R60, R62, R66, R103 | Res Thick Film 0402 100 Ohm 1% 0.1W(1/10W) ±100ppm/C Molded SMD Automotive T/R | ERJ-2RKF1000X | 16
Fitted | R3, R11A, R11B, R11C, R11D, R13, R14, R15, R44, R45, R48, R51, R61, R65 | Res Thick Film 0402 0 Ohm Molded SMD Automotive T/R | ERJ-2GE0R00X | 14
Fitted | R8, R9, R10 | RES SMD 49.9 OHM 1% 1/16W 0402 | RC0402FR-0749R9L | 3
Fitted | R16, R29, R31, R32, R33, R34, R35, R37, R55, R97, R98, R100, R101, R102 | Res Thick Film 0402 10K Ohm 1% 0.063W(1/16W) ±100ppm/C Molded SMD T/R | RC1005F103CS | 14
Fitted | R28, R36, R39 | Res Thick Film 0402 4.7K Ohm 1% 1/16W ±100ppm/C Molded SMD T/R | RC1005F472CS | 3
Fitted | R30 | Res Thick Film 0402 200K Ohm 1% 0.1W(1/10W) ±100ppm/C Molded SMD Automotive T/R | ERJ-2RKF2003X | 1
Fitted | R40A, R40B, R41A, R41B | Res Thick Film 0402 330 Ohm 1% 0.1W(1/10W) ±100ppm/C Molded SMD Automotive Punched T/R | ERJ-2RKF3300X | 4
Fitted | R46, R49, R50, R53, R56, R63 | Res Thick Film 0402 102K Ohm 1% 0.1W(1/10W) ±100ppm/C Molded SMD Automotive T/R | ERJ-2RKF1023X | 6
Fitted | R47 | PANASONIC ELECTRONIC COMPONENTS ERJ2RKF3012X SMD Chip Resistor, Thick Film, 30.1 kohm, 50 V, 0402 [1005 Metric], 100 mW, 1%, ERJ2R Series | ERJ-2RKF3012X | 1
Fitted | R52 | RES SMD 11K OHM 1% 1/16W 0402 | RC0402FR-0711KL | 1
Fitted | R54 | RES SMD 1K OHM 1% 1/16W 0402 | RC0402FR-071KL | 1
Fitted | R58 | Res Thick Film 0402 15K Ohm 1% 0.1W(1/10W) ±100ppm/C Molded SMD Automotive Punched T/R | ERJ-2RKF1502X | 1
Fitted | R59 | Panasonic ERJ2RK Series Thick Film Surface Mount Fixed Resistor 0402 Case 1% 0.1W 100ppm/C | ERJ-2RKF1602X | 1
Fitted | R64 | Res Thick Film 0402 40.2K Ohm 1% 0.1W(1/10W) ±100ppm/C Molded SMD Automotive T/R | ERJ-2RKF4022X | 1
Fitted | R99 | Res Thick Film 0402 10 Ohm 1% 0.1W(1/10W) ±100ppm/C Molded SMD Automotive Punched T/R | ERJ-2RKF10R0X | 1
Fitted | RF CASE | LEADER TECH-FERRISHIELD SMS-462C SURFACE MOUNT SHIELD COVER, RECT New | SMS-462C | 1
Fitted | RFS1 | LEADER TECH-FERRISHIELD SMS-462F SURFACE MOUNT SHIELD FRAME, RECT New | SMS-462F | 1
Fitted | U1A, U1B, U1C, U1D | IC AFE 24BIT 16KSPS LN 64TQFP | ADS1299IPAGR | 4
Fitted | U2A, U2B, U2C, U2D, U3A, U3B, U3C, U3D, U6, U7, U14 | TVS DIODE 5.5VWM 14.5VC SC70-6 | TPD4E1B06DCKR | 11
Fitted | U4 | IC REG LDO 3.3V 0.8A SOT223 | LD1117S33CTR | 1
Fitted | U5 | IC OPAMP GP 1.4MHZ RRO SOT23-5 | TSV321RILT | 1
Fitted | U8A, U8B | IC USB FS SERIAL UART 28-SSOP | FT232RL-REEL | 2
Fitted | U10 | Charge Pump Switching Regulator IC Positive and Negative (Dual Rail) Adjustable -5V, 1.5V 2 - Dual Output 250mA 12-WFDFN Exposed Pad | LM27762DSST | 1
Fitted | U11 | IC VREF SERIES 2.5V SOT23-3 | REF3025AIDBZR | 1
Fitted | U12 |  | PCF8563T/5,518 | 1
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

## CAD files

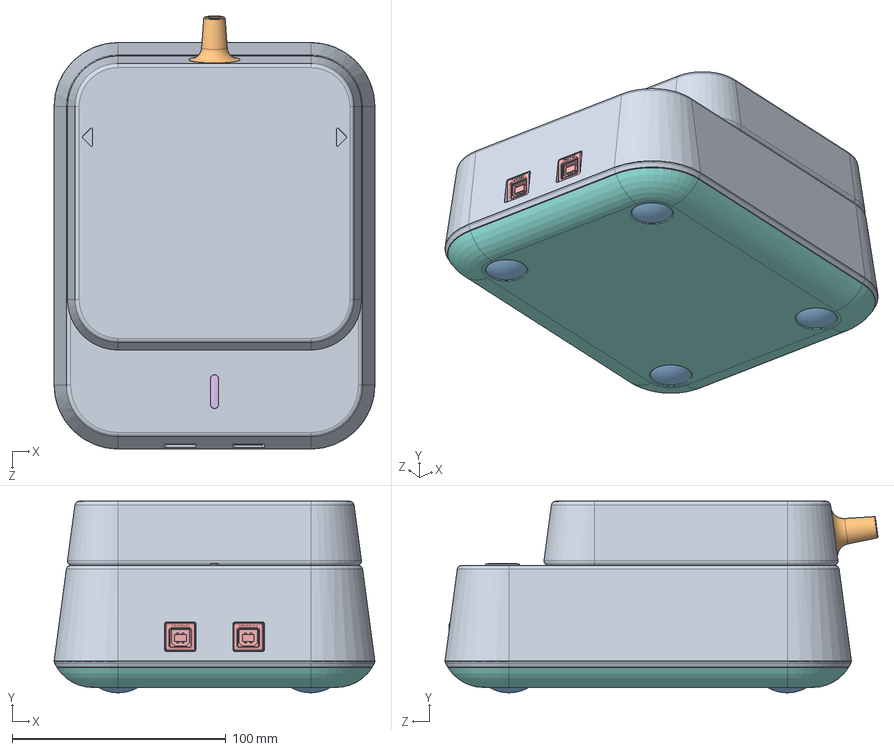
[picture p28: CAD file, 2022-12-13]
hardware/mechanical/bioamp/710-03064-01_Rev03_6-26-2019/FullComponentAssem.SLDASM
149.9 x 89.5 x 202.3 mm
LITEactivebreakoutboard02oct2018
LITEsingleboard27sep2018
new_690-13335-01

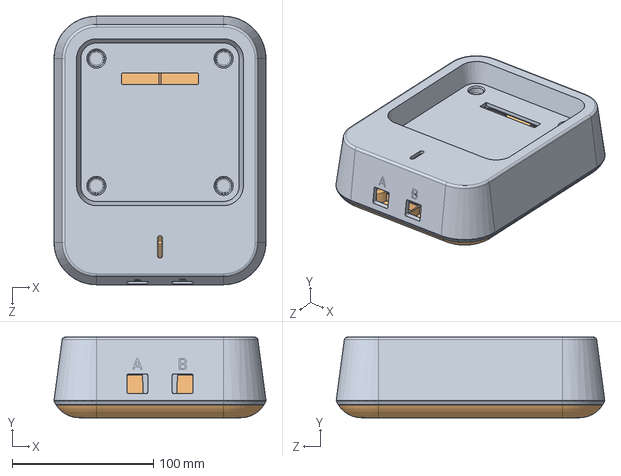
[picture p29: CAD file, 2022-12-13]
hardware/mechanical/bioamp/710-03064-01_Rev03_6-26-2019/AmpCheckAssem.SLDASM
149.9 x 57.0 x 189.9 mm
01-ButterAmpTop
01-ButterAmpBottom

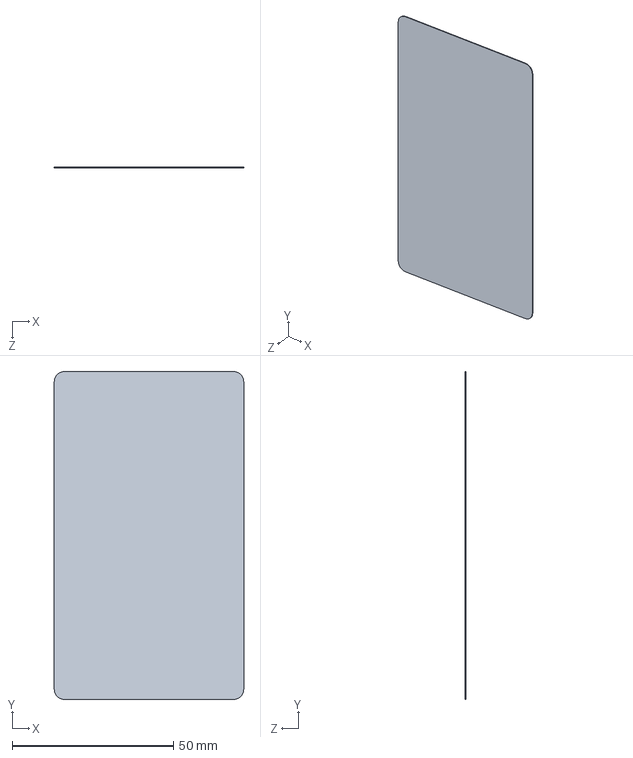
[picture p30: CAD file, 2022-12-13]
hardware/mechanical/bioamp/710-03064-01_Rev03_6-26-2019/961-00019-01.SLDASM
58.7 x 101.6 x 0.254 mm

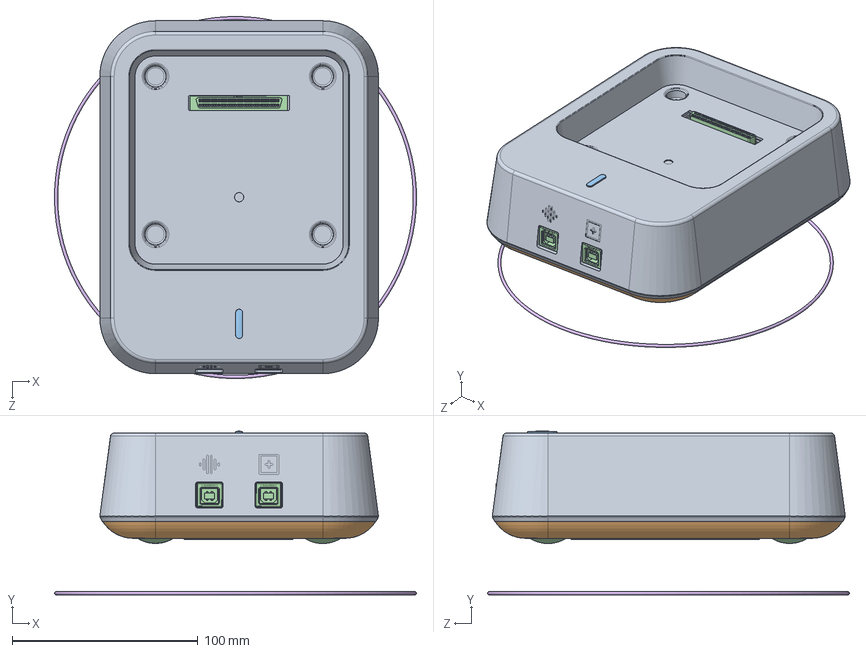
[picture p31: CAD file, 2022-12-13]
hardware/mechanical/bioamp/710-03064-01_Rev03_6-26-2019/710-03064-01.SLDASM
194.8 x 88.1 x 194.8 mm
O-RING PLACE HOLDER

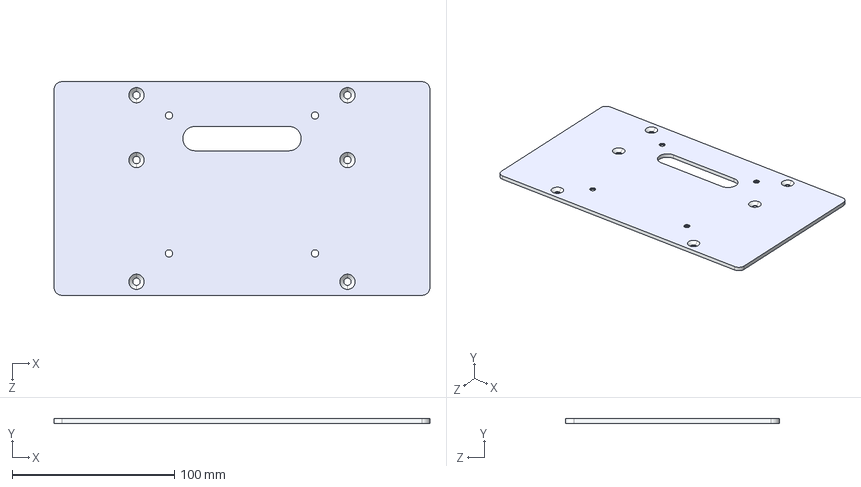
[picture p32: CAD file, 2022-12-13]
hardware/assembly/bioamp_alignment_tools/drawings_Connector Alignment Tool/690-14170-01_MECH, FIXTURE, CONNECTOR ALIGNMENT PLATE, AMBER.STEP
231.7 x 3.00 x 131.7 mm

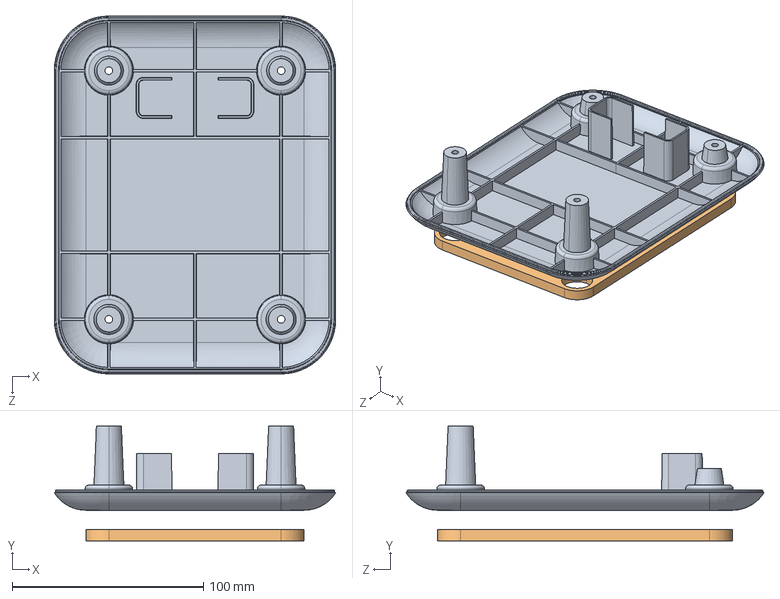
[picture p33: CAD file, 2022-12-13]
hardware/assembly/bioamp_alignment_tools/drawings_Label Alignment Tool/690-14168-01_rev01_MECH, FIXTURE, LABEL ALIGNMENT, AMBER.STEP
147.1 x 60.0 x 187.1 mm

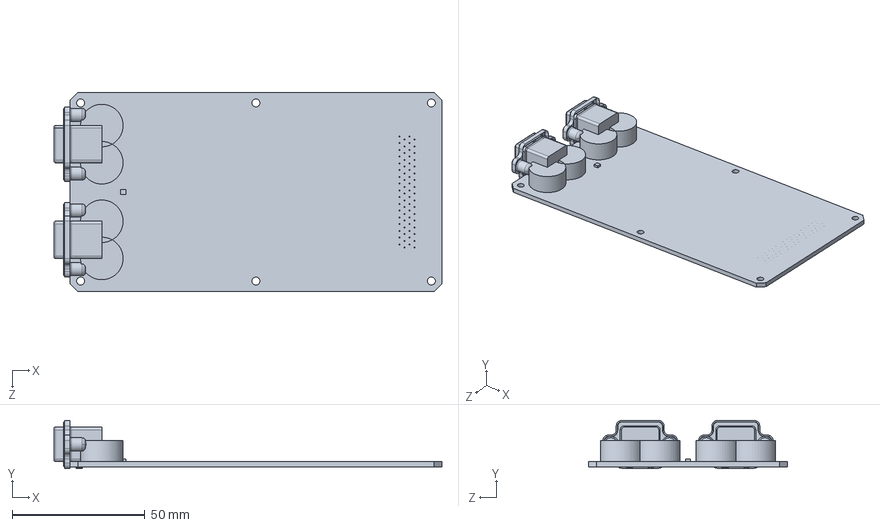
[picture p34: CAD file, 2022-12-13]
hardware/electronic/bioamp/gerbers/Mechanical/HTCBoardSTEP203-24SEP.SLDPRT
146.0 x 18.1 x 75.0 mm

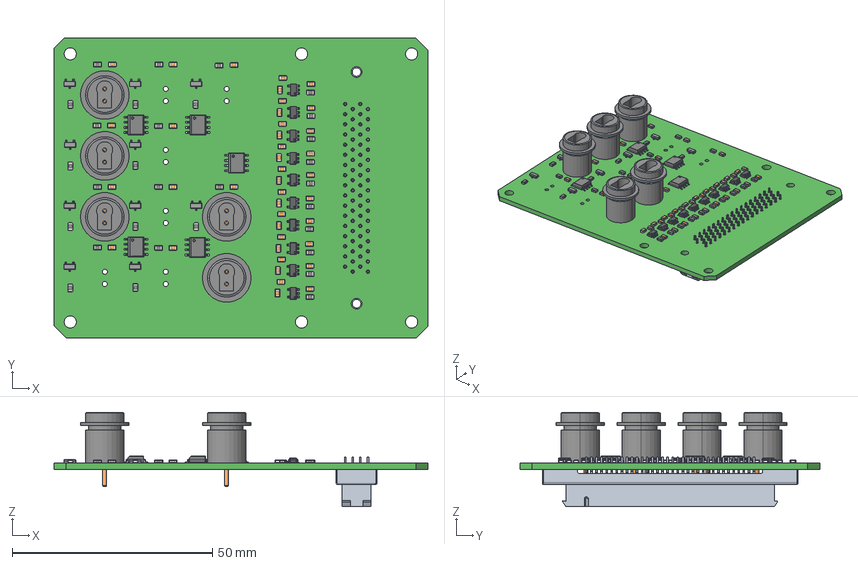
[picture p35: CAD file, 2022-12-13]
hardware/electronic/schematics_and_pcb_files/Active Sensor BB Rev 3.1/Outputs/Active Sensor BB R3.1 Production Files/ExportSTEP/Active Sensor BB(PRODUCTION).step
93.5 x 75.0 x 23.6 mm
Board
c-2-5174339-5-a-3d
plastics1_connector x 5
SW3dPS-0805_SMD_Capacitor x 40
User_Library-sot-3p290x130ll237h100 x 10
SW3dPS-0805_SMD_Resistor x 30
User_Library-SOIC-8_SOIC-8_Body_1 x 5
User_Library-SOIC-8_SOIC-8_Pins_1 x 5
User_Library-SOT23-5-1 x 10

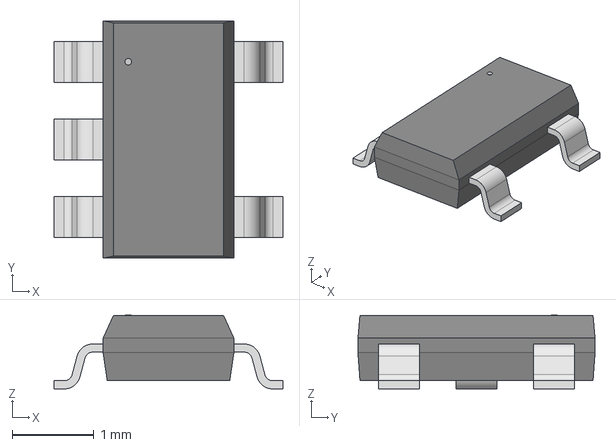
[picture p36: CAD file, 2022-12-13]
hardware/electronic/sensor_strip/gerbers_and_bom/AD8603AUJZR2/2019-02-05_22-09-43/STEP/UJ_5.step
2.80 x 2.90 x 0.903 mm

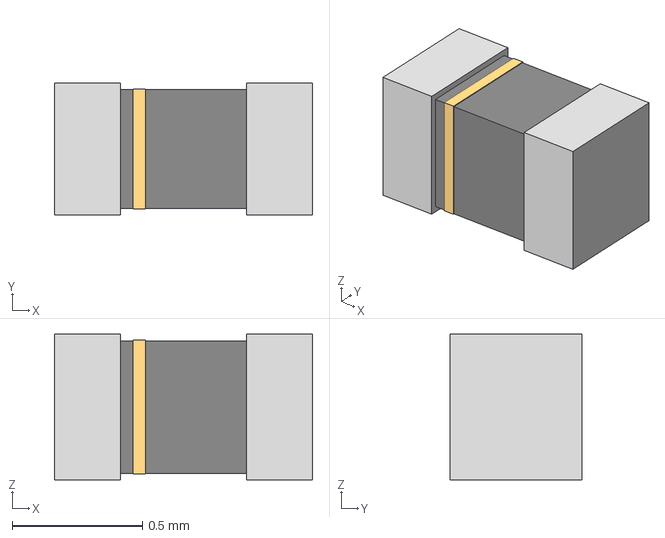
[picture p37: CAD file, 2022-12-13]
hardware/electronic/sensor_strip/gerbers_and_bom/C0402C241J3GAC7867/STEP/G-155.step
0.99 x 0.508 x 0.559 mm

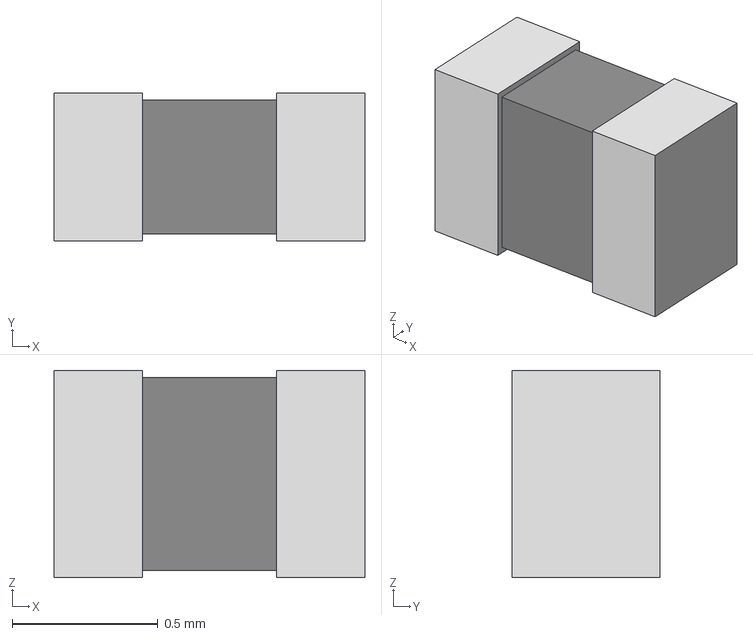
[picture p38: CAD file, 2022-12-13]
hardware/electronic/sensor_strip/gerbers_and_bom/RC0402JR0710KL/2019-02-05_20-48-00/STEP/RC0402N-M.step
1.07 x 0.508 x 0.711 mm

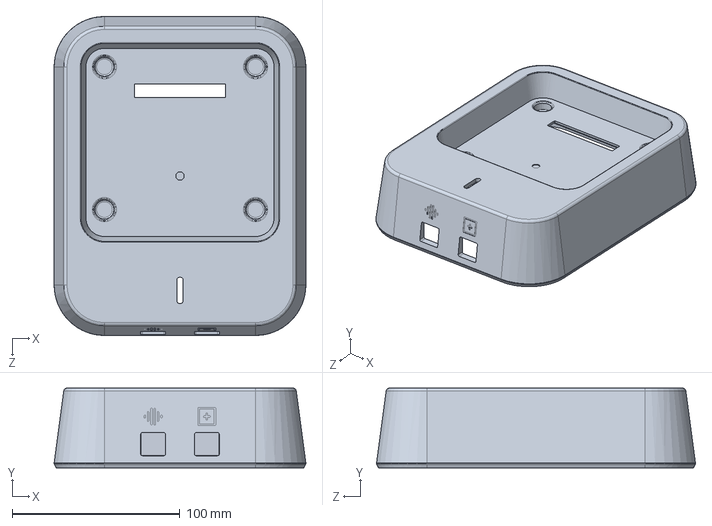
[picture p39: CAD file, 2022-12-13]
hardware/mechanical/bioamp/710-03064-01_Rev03_6-26-2019/690-13322-01.SLDPRT
149.9 x 47.5 x 189.9 mm

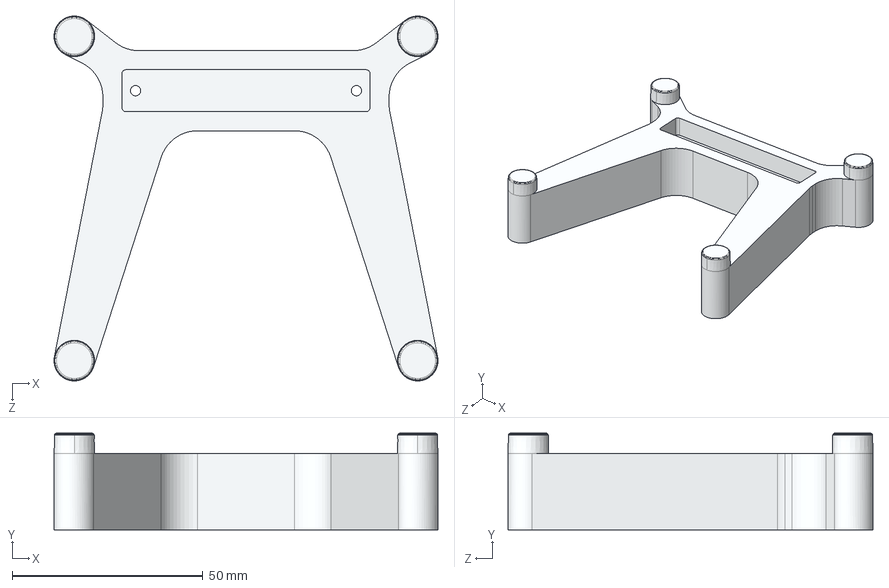
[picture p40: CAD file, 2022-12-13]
hardware/assembly/bioamp_alignment_tools/drawings_Connector Alignment Tool/690-14180-01_rev01_MECH, FIXTURE, CONNECTOR ALIGNMENT, AMBER.STEP
100.6 x 25.3 x 95.7 mm

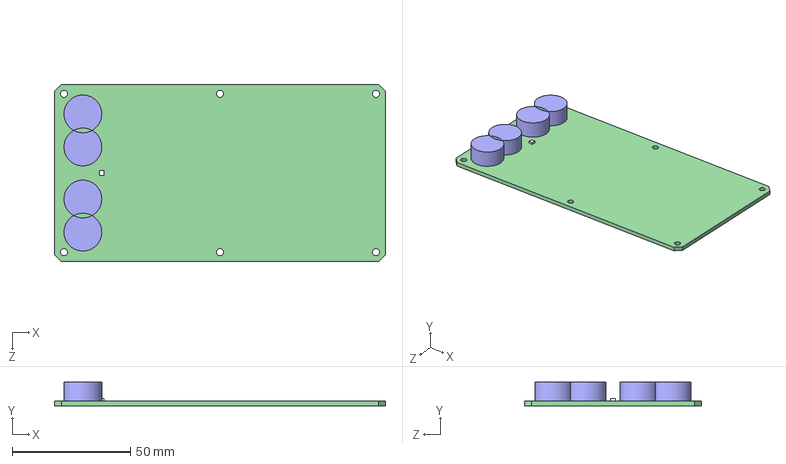
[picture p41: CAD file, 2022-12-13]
hardware/electronic/bioamp/gerbers/Mechanical/ComponentLayoutHaden20SEP.STEP
140.0 x 10.0 x 75.0 mm

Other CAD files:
hardware/electronic/bioamp/gerbers/Pcb/Luchador Pcb.DWG
hardware/electronic/schematics_and_pcb_files/Luchador Rev 3.2b/Pcb/Luchador Pcb.DWG
hardware/electronic/bioamp/gerbers/Mechanical/ComponentLayoutHaden20SEP.DXF
hardware/electronic/bioamp/gerbers/Mechanical/ComponentLayoutHaden20SEP.SLDPRT
hardware/electronic/schematics_and_pcb_files/Luchador Rev 3.2b/Mechanical/ComponentLayoutHaden20SEP.DXF
hardware/electronic/schematics_and_pcb_files/Luchador Rev 3.2b/Mechanical/ComponentLayoutHaden20SEP.SLDPRT
hardware/electronic/sensor_strip/gerbers_and_bom/AD8603AUJZR2/2019-02-05_22-09-43/STEP/UJ_5-L.step
hardware/electronic/sensor_strip/gerbers_and_bom/AD8603AUJZR2/2019-02-05_22-09-43/STEP/UJ_5-M.step
hardware/electronic/sensor_strip/gerbers_and_bom/C0402C241J3GAC7867/STEP/G-155-L.step
hardware/electronic/sensor_strip/gerbers_and_bom/C0402C241J3GAC7867/STEP/G-155-M.step
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

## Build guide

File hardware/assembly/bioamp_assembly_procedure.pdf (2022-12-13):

Work Instructions M20 Bioamp - Butter Dish

Title | M20 Bioamp (Butter Dish) Assembly Instructions

P/N

Scope | Assembly instructions for Flex

Revision

Date

Author

Approver(s):

Revision History

01 | Initial Release

02

03

04

Tool / Consumable List

Description

Consumables | Tools
| T8 torque driver
| T15 torque driver
| USB A/B Cable
| Laptop (power source)
| Connector Alignment Fixture
| Sticker Placement Jig
| DYMO Printer

Seq # | Cycle Time | Operation Description | Power board via USB connection to laptop, check all LEDs are illuminated (10 in total) ● 1 green power indicator lit ● 5 rail indicators lit ● 4 chips are lit

01

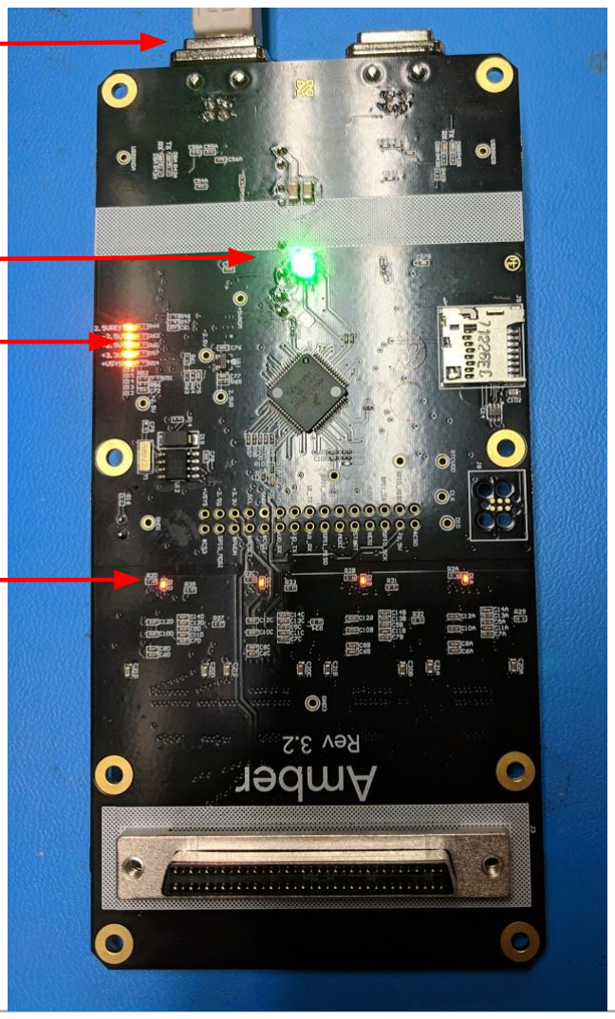
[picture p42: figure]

| Part Desc: | Part#
| Amber Board | BOM-0098-00
| Tools/Equipment: | Part#
| USB A/B with power source

Critical Process Parameters

Critical Quality Attributes

All LED lights specified should be illuminated

Key Points

Should any LEDs fail to illuminate, note which component and place board in MRB

Power indicator (1x)

Rail indicators (5x)

A-D chips (x4)

Input power

Seq # | Cycle Time | Operation Description | Place lightpipe gasket on lightpipe Note: Gasket is not symmetric and only fits in one orientation

02

| Part Desc: | Part#
| Lightpipe Lightpipe Gasket | PN-0169-00 PN-0170-00
| Tools/Equipment: | Part#

Critical Process Parameters

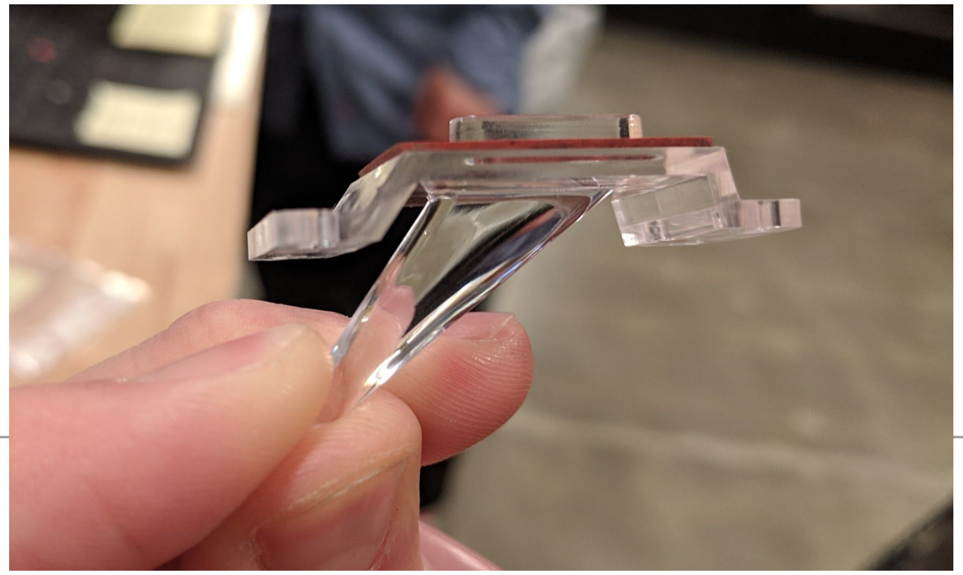
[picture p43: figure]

Critical Quality Attributes

Key Points

Gasket spacing is not symmetric, ensure it is placed in the correct orientation

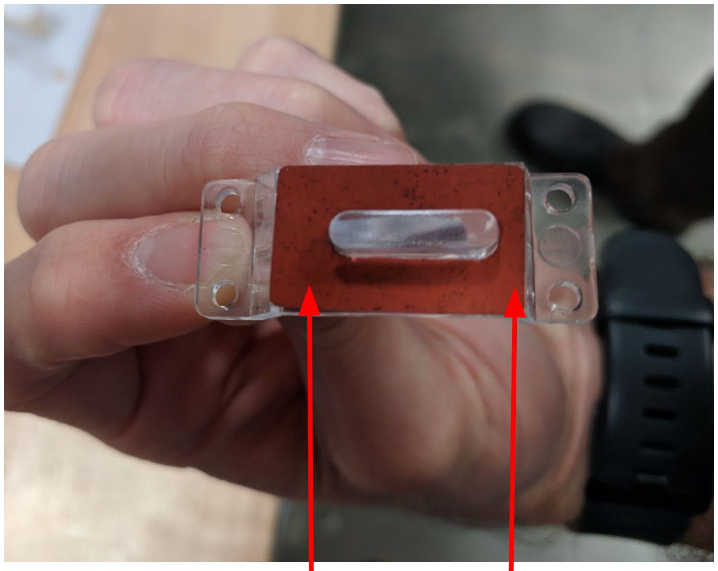
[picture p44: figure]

Non-symmetric gasket

Seq # | Cycle Time | Operation Description | Place lightpipe with gasket on top housing, secure using qty 4 M2.63x6mm screws, tighten to 35 in-oz Note: actual gasket will likely be red color instead of gray as shown

03

| Part Desc: | Part#
| Lightpipe Lightpipe Gasket Bioamp Top Housing Torx M2.63x6 (x4) | PN-0169-00 PN-0170-00 PN-0166-00 PN-0104-00
| Tools/Equipment: | Part#
| T8 torque driver

Critical Process Parameters

35 in-oz tightening torque

Critical Quality Attributes

Ensure screw head is seated and flush with lightpipe surface

Key Points

Tall end of lightpipe faces inward (only fits in one orientation) Fasten in star pattern

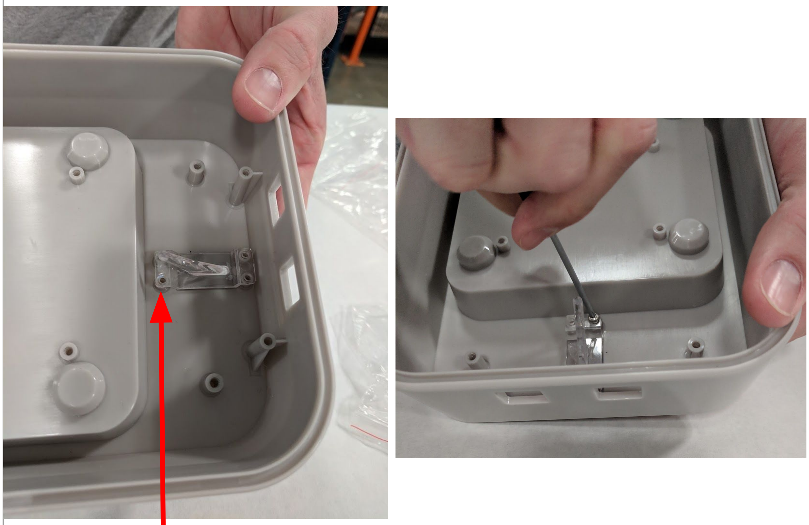
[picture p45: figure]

Tall end of horn
points inward

Seq # | Cycle Time | Operation Description | Place qty 2 USB gaskets around USB connectors on main board

04

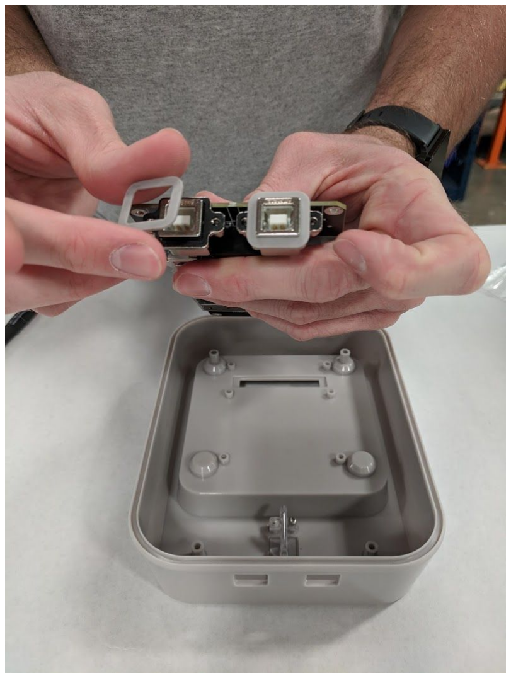
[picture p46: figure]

| Part Desc: | Part#
| USB Gasket (x2) Amber Board | PN-0213-00 BOM-0098-00
| Tools/Equipment: | Part#

Critical Process Parameters

Critical Quality Attributes

Key Points

Seq # | Cycle Time | Operation Description | Place connector boot on large connector

05

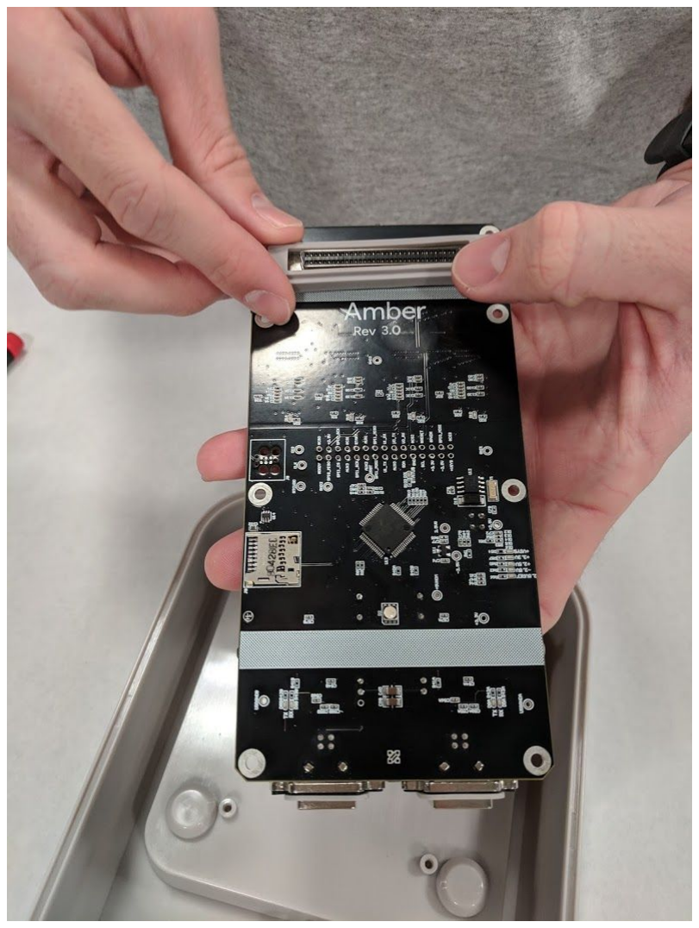
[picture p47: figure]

| Part Desc: | Part#
| Connector Boot Amber Board | PN-0171-00 BOM-0098-00
| Tools/Equipment: | Part#

Critical Process Parameters

Critical Quality Attributes

Key Points

Seq # | Cycle Time | Operation Description | Place top housing on connector alignment fixture

06

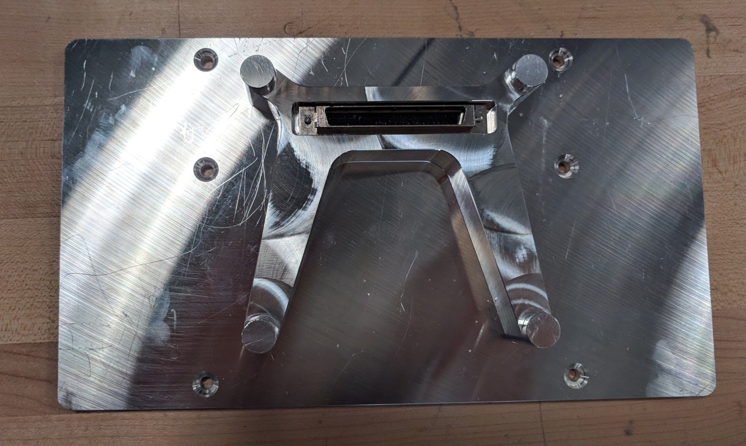
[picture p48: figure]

| Part Desc: | Part#
| Bioamp Top Housing | PN-0166-00
| Tools/Equipment: | Part#
| Alignment Fixture | N/A

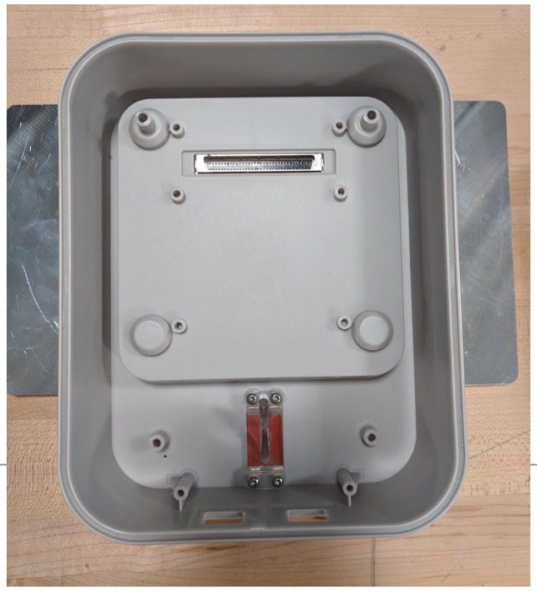
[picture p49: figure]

Critical Process Parameters

Critical Quality Attributes

Key Points

Seq # | Cycle Time | Operation Description | Line up USB connectors with cutouts in top housing, push board forward then down to secure in place. Board should make full contact with connector from alignment fixture.

07

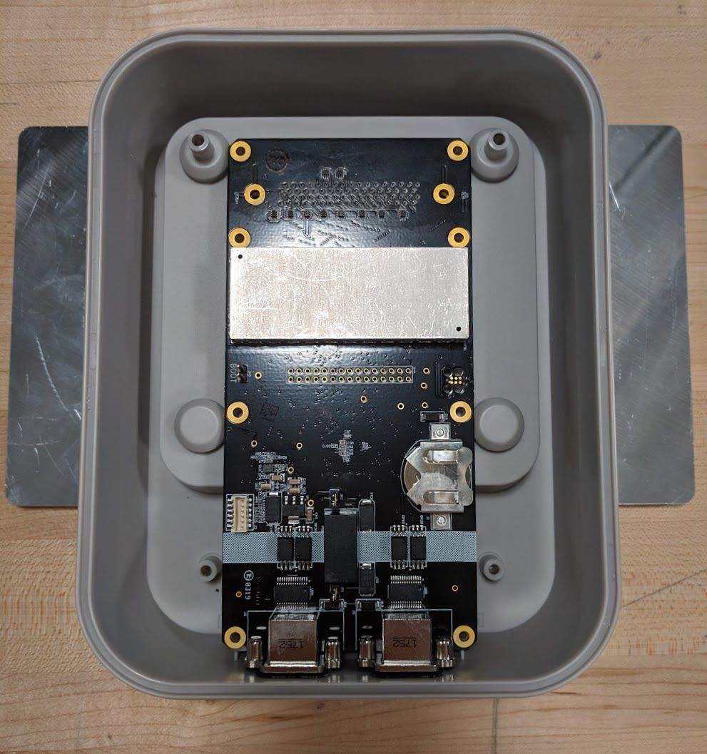
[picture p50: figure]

| Part Desc: | Part#
| Amber Board Top Housing | BOM-0098-00 PN-0166-00
| Tools/Equipment: | Part#
| Connector Alignment Fixture | TBD

Critical Process Parameters

Critical Quality Attributes

Key Points

Seq # | Cycle Time | Operation Description | Fasten qty 4 M2.63x6 screws in connector region to 35 in-oz. Tighten in star pattern in the order shown below. Remove assembly from alignment fixture.

08

| Part Desc: | Part#
| Amber Board Top Housing Torx M2.63x6 (x4) | BOM-0098-00 PN-0166-00 PN-0104-00
| Tools/Equipment: | Part#
| T8 torque driver

Critical Process Parameters

35 in-oz tightening torque

Critical Quality Attributes

Ensure screw head is seated and flush with board surface

Key Points

Torque in star pattern

3 | 2
1 | 4

Seq # | Cycle Time | Operation Description | Working your way towards USB connectors, fasten two middle screws then two USB-side screws with qty 4 M2.63x6 screws to 35 in-oz

09

| Part Desc: | Part#
| Amber Board Top Housing Torx M2.63x6 (x4) | BOM-0098-00 PN-0166-00 PN-0104-00
| Tools/Equipment: | Part#
| T8 torque driver

Critical Process Parameters

35 in-oz tightening torque

Critical Quality Attributes

Ensure screw head is seated and flush with board surface

Key Points

Fasten screws near USBs last to ensure board does not buckle
Ensure all 4 screws are tightened after assembly is removed from alignment fixture

Fasten first

Fasten last

Seq # | Cycle Time | Operation Description | Insert the o-ring along the groove at the edge of the top housing

10

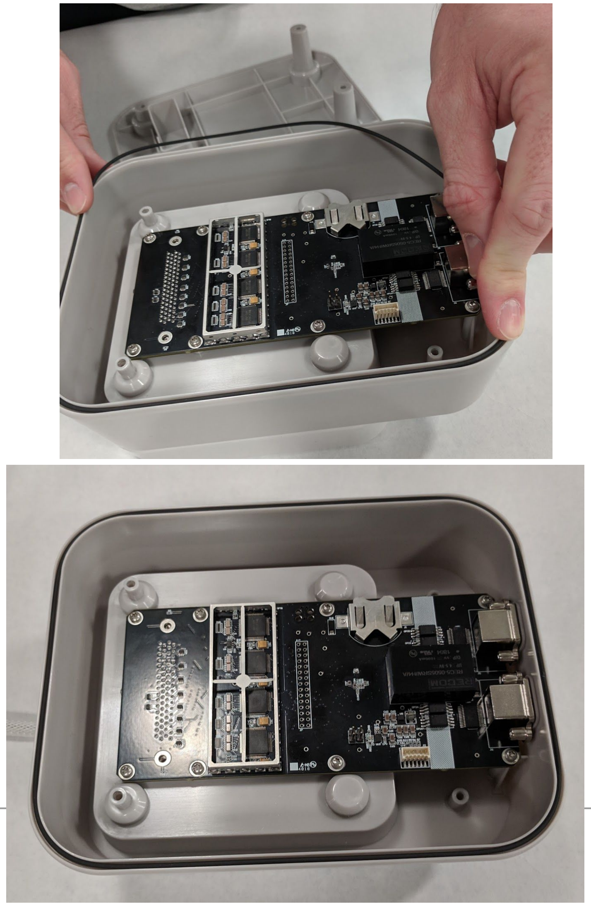
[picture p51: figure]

| Part Desc: | Part#
| Top Housing O-ring | PN-0166-00 PN-0293-01
| Tools/Equipment: | Part#

Critical Process Parameters

Critical Quality Attributes

Ensure o-ring is securely within groove

Key Points

Seq # | Cycle Time | Operation Description | Place bottom housing, tightly squeeze top and bottom together and secure using qty 4 M3.36x10 screws to 8.5 in-lbs. Tighten in a star pattern. Ensure the enclosure is fully secured by squeezing together, no movement should be felt. Note: Bottom housing will only fit in one orientation

11

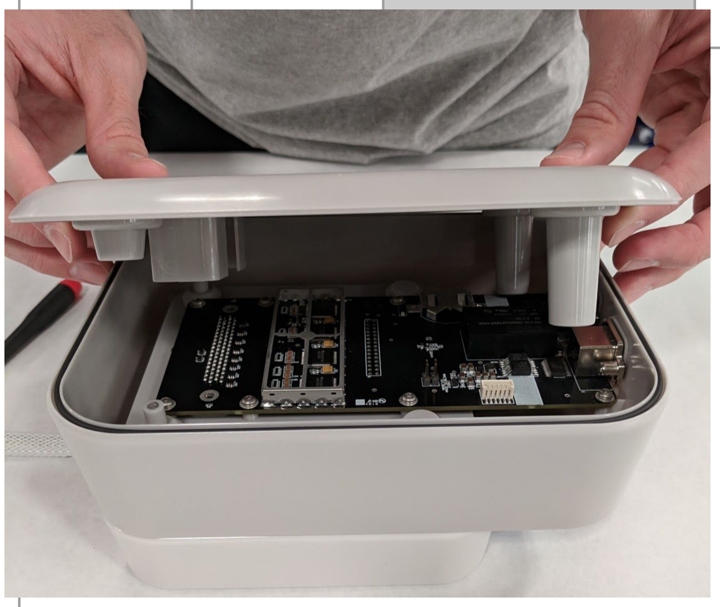
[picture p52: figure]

| Part Desc: | Part#
| Top Housing Bottom Housing Torx M3.36x10 (x4) | PN-0166-00 PN-0165-00 PN-0216-00
| Tools/Equipment: | Part#
| T15

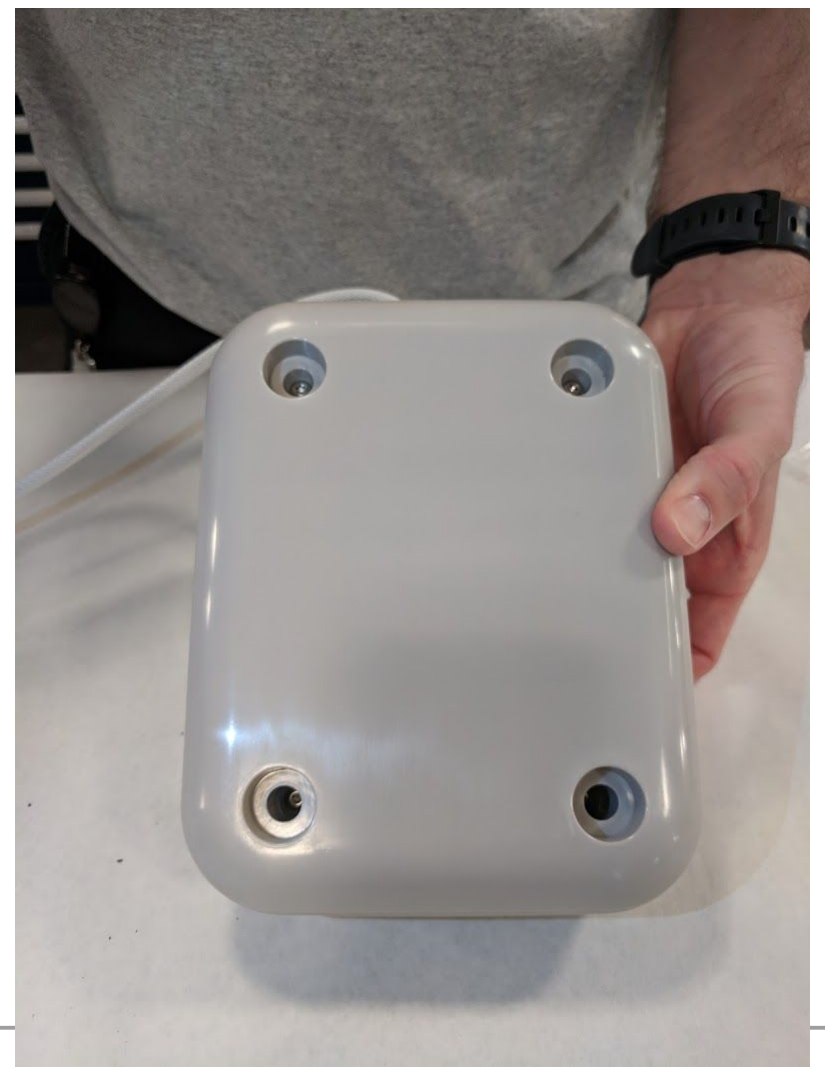
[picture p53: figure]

Critical Process Parameters

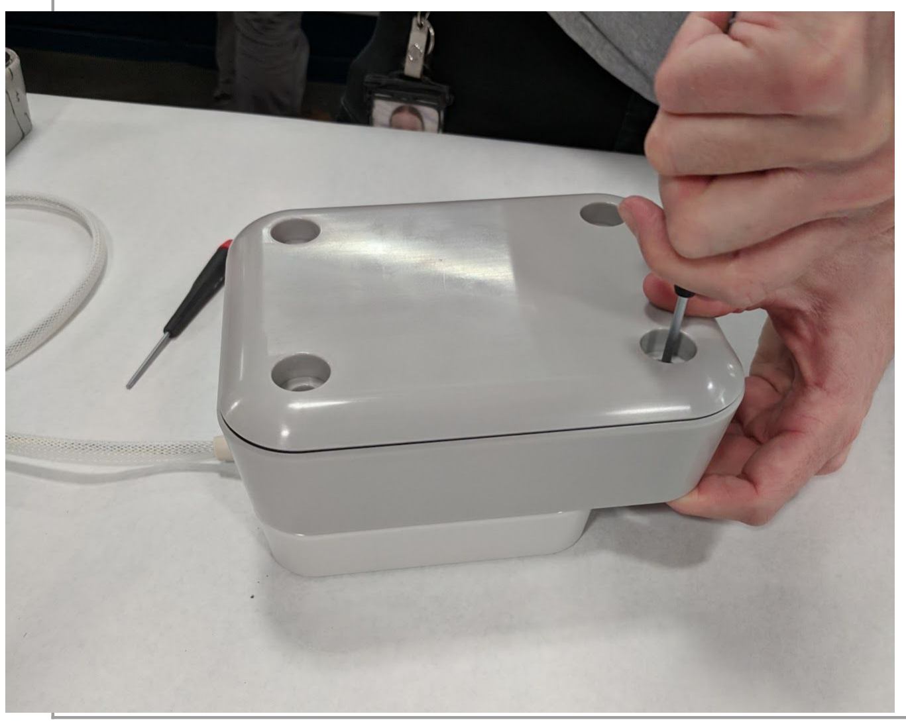
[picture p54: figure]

Enough pressure needs to be applied between top and bottom housings to compress o-ring and create seal

Critical Quality Attributes

Ensure screws are fully seated 8.5 in-lbs tightening torque

Key Points

After tightening, you should not feel any movement when squeezing top and bottom enclosures together

Seq # | Cycle Time | Operation Description | Attach pre-cut VHB disc to bottom surface of each rubber foot (qty 4), remove backing

12

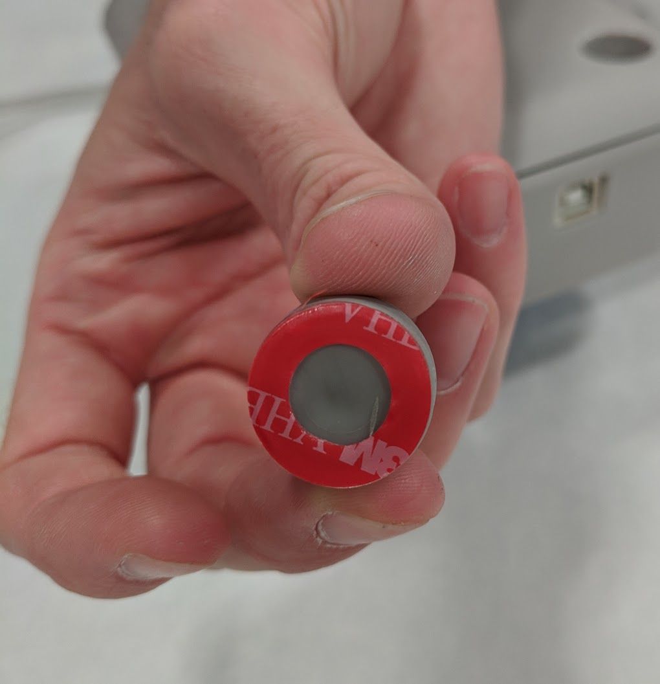
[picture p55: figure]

| Part Desc: | Part#
| Rubber Foot (x4) VHB Pre-cut disc | PN-0172-00 PN-0299-00
| Tools/Equipment: | Part#

Critical Process Parameters

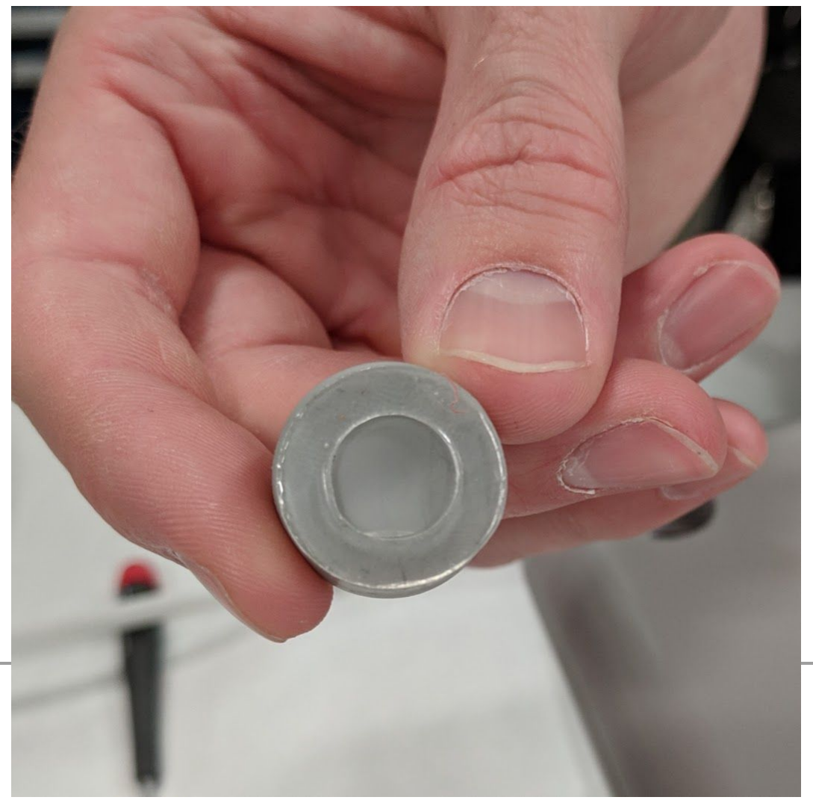
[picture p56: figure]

Critical Quality Attributes

Key Points

Seq # | Cycle Time | Operation Description | Confirm that 4 screws are fully seated and there is no excess gap between housings. Then, firmly press each rubber foot until it is seated in bottom housing

13

| Part Desc: | Part#
| Rubber Foot (x4) Bottom Housing | PN-0172-00 PN-0165-00

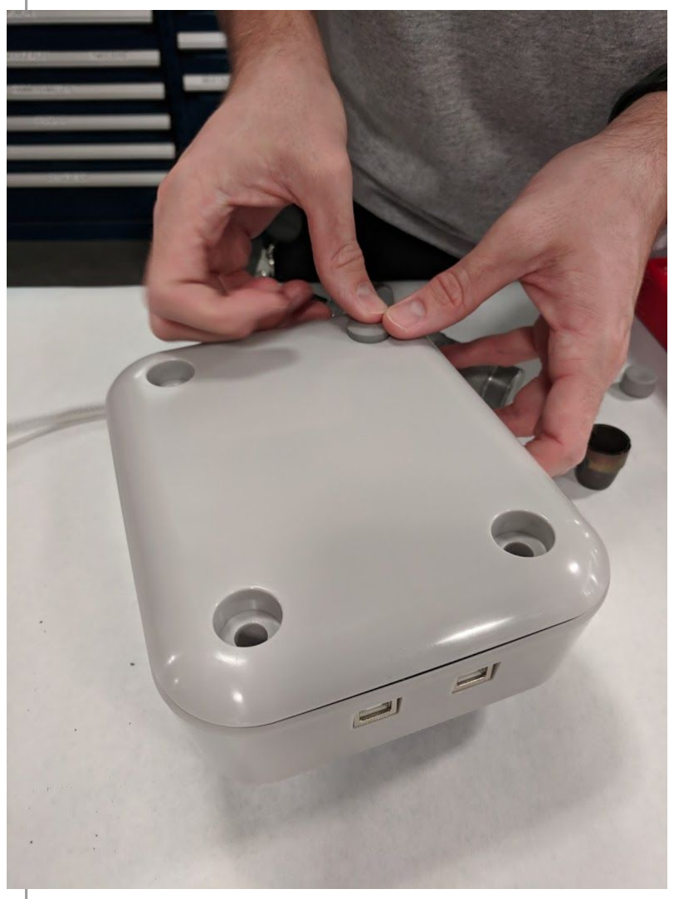
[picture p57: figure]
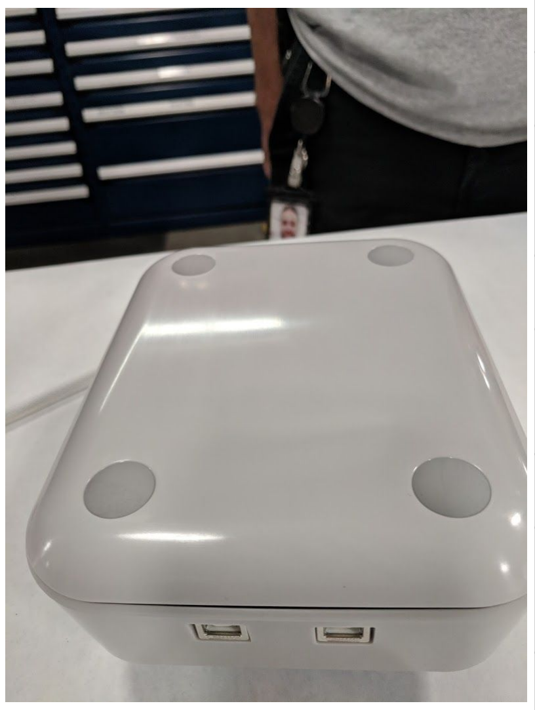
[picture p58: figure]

| Tools/Equipment: | Part#

Critical Process Parameters

Critical Quality Attributes

Key Points

Little rubber feet must sit completely in bore with outer circumference not protruding above housing surface

Seq # | Cycle Time | Operation Description | Create a label sticker using the DYMO program following the model below. The serial number of the amp should be BYYMMDD##, where YY are the last two digits of the current year, MM are the current month, DD are the current day, and ## are the number in sequence of amps you have made this day (starting with 01). After printing, affix sticker to underside of amp. Use the jig to place the sticker. The top of the sticker should be towards the connector end of the device

14

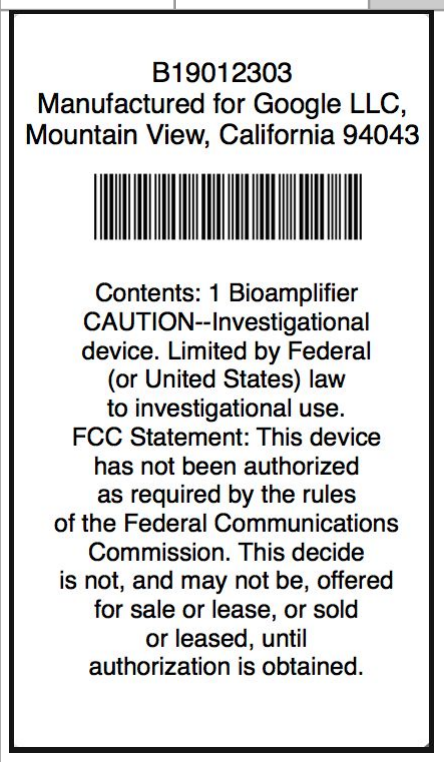
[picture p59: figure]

| Part Desc: | Part#

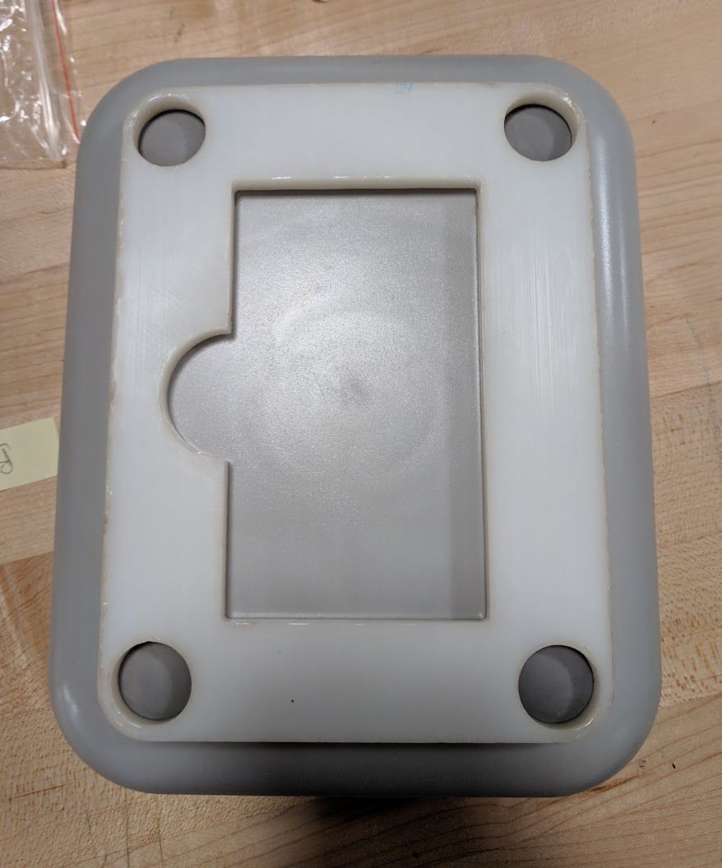
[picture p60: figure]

Tools/Equipment: | Part#

DYMO printer Sticker Placement Jig

Critical Process Parameters

Critical Quality Attributes

Key Points

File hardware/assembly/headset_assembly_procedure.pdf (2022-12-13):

990-03957-00 Work Instructions M20 Adapter - Butter Stick

Title | 990-03957-00 - DOC, M20 WORK INSTRUCTIONS ADAPTER - BUTTER STICK, AMBER
P/N | 710-03085-02_rev01_ASSY, ELEC-MECH, M20 HEADSET, BUTTER STICK, AMBER
Scope | Assembly instructions for Flex
Revision | 1
Date | 2019-12-20

Author

Approver(s):

Revision History

01 | Initial Release

02

03

04

Work Instructions M20 Adapter - Butter Stick

Tool / Consumable List

Description

Consumables | Tools
| T8 torque driver
| T15 torque driver

# Bottom Sub-Assembly

## Note: Bottom and top sub-assemblies are

## independent and not sequential

Seq # | Cycle Time | Operation Description | Place connector boot around large connector

01

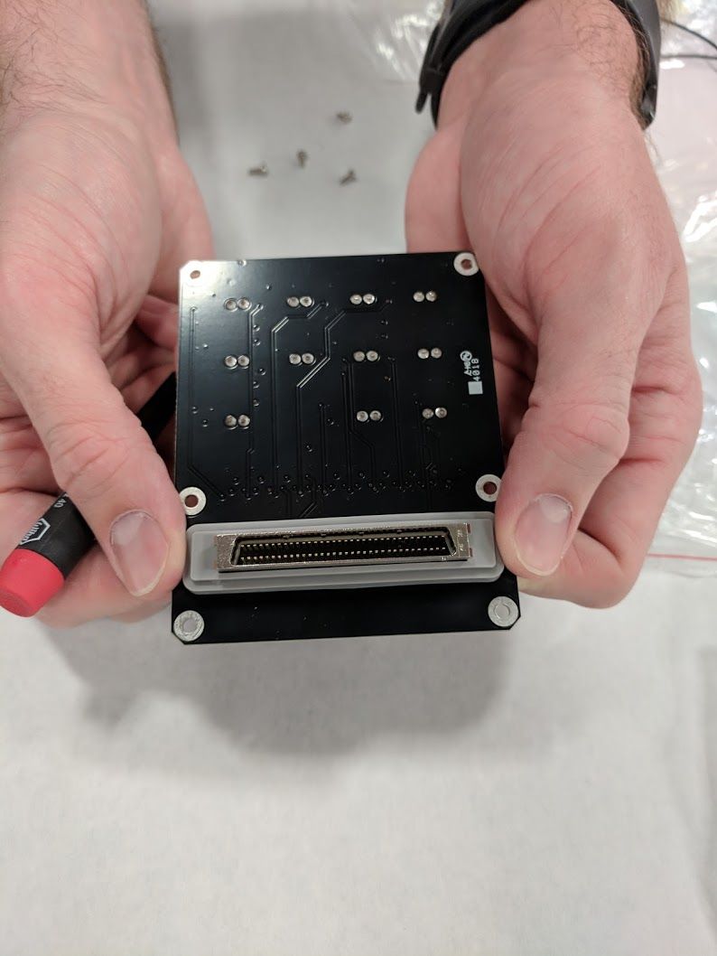
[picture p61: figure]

| Part Desc: | Part#
| Connector Boot Breakout Board | PN-0171-00 ASM-0282-00
| Tools/Equipment: | Part#

Critical Process Parameters

Critical Quality Attributes

Key Points

Seq # | Cycle Time | Operation Description | Place Breakout Board on bottom housing using 3 alignment pins as guidance. Hold board in place through affixing screws so it does not shift.

02

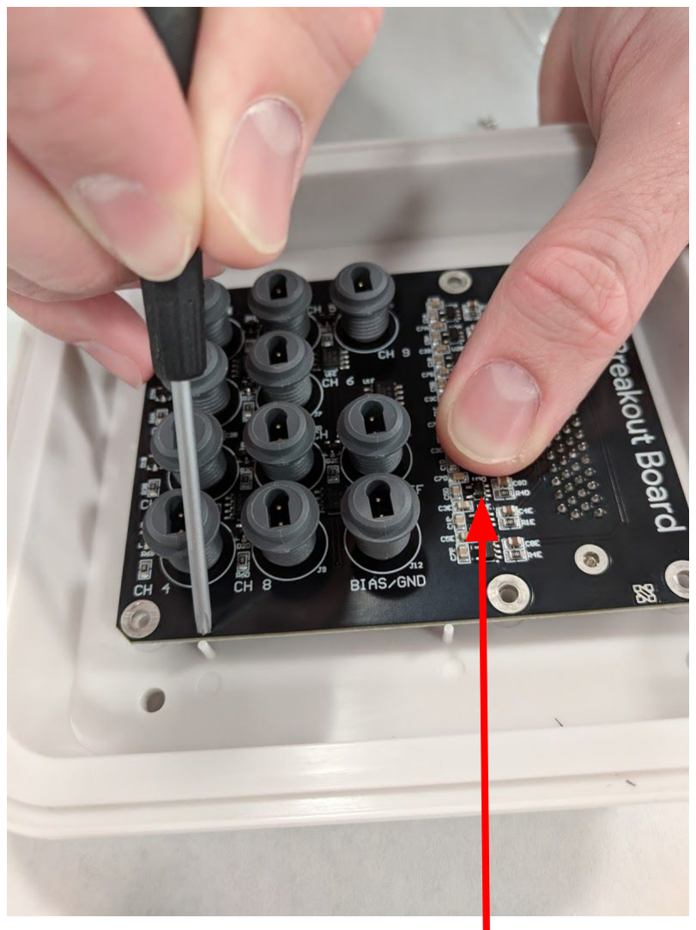
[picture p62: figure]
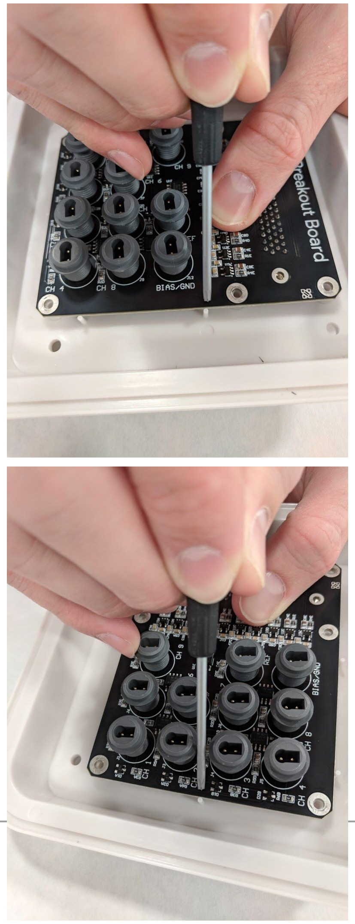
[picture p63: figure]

| Part Desc: | Part#
| Breakout Board Bottom Housing | ASM-0282-00 PN-0163-00
| Tools/Equipment: | Part#

Critical Process Parameters

Critical Quality Attributes

Key Points

Alignment pins are flexible so take caution not to apply excessive force when aligning board

Hold in place until screws are fastened

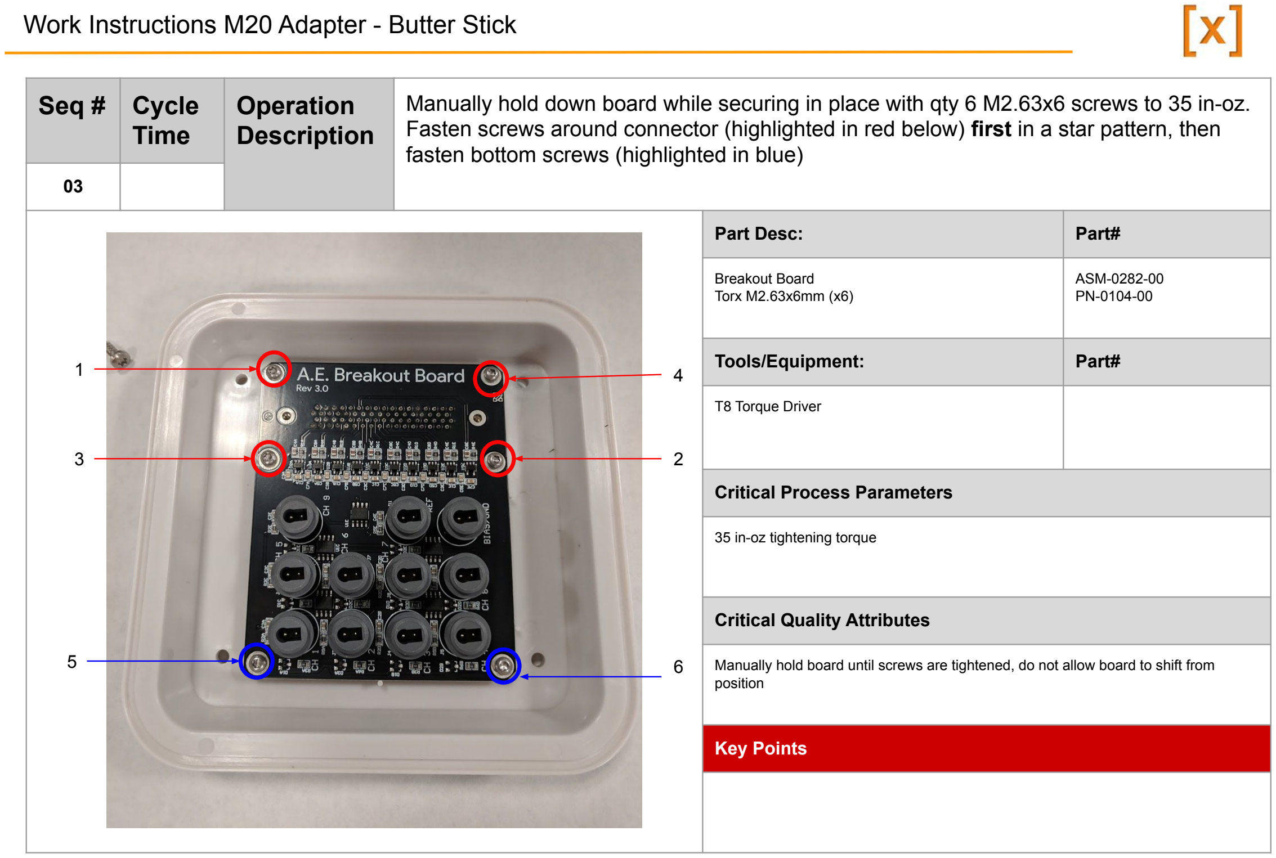
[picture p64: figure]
Part Desc:; Part#; Breakout Board Torx M2.63x6mm (x6); ASM-0282-00 PN-0104-00; Tools/Equipment:; T8 Torque Driver; Critical Process Parameters; 35 in-oz tightening torque; Critical Quality Attributes; position; Key Points

Seq # | Cycle Time | Operation Description | Manually hold down board while securing in place with qty 6 M2.63x6 screws to 35 in-oz. Fasten screws around connector (highlighted in red below) first in a star pattern, then fasten bottom screws (highlighted in blue)

Manually hold board until screws are tightened, do not allow board to shift from

Seq # | Cycle Time | Operation Description | Insert o-ring around the groove at the edge of the bottom housing

04

| Part Desc: | Part#

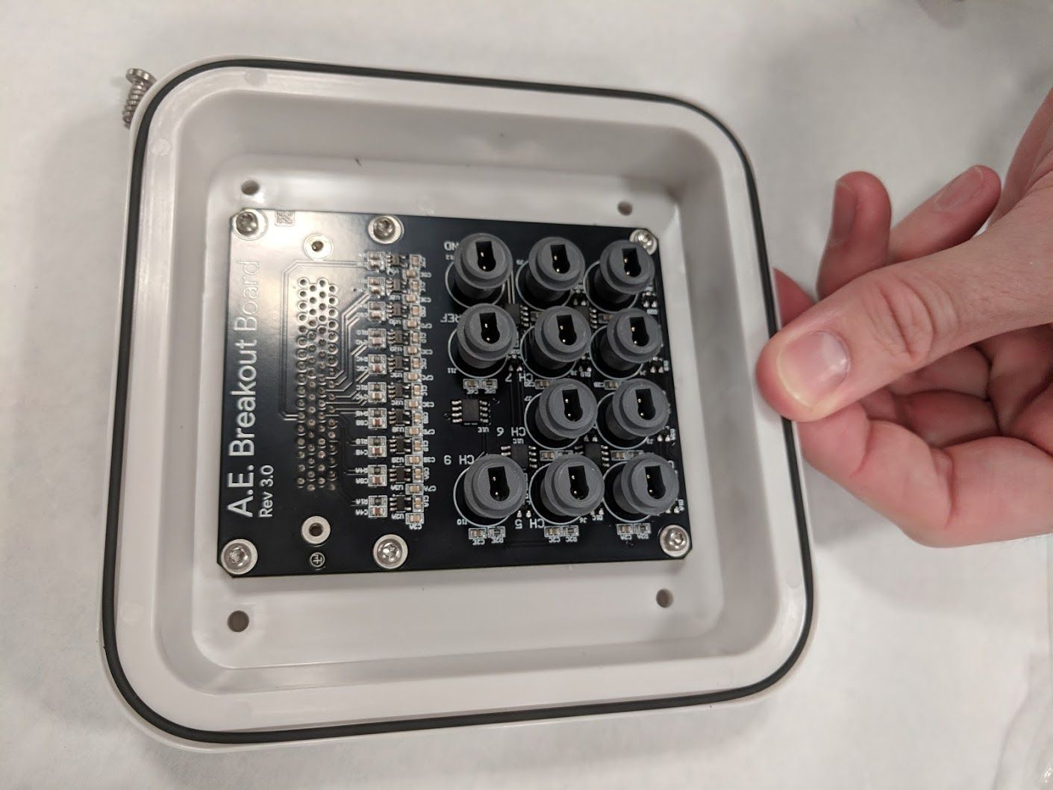
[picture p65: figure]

| O-ring Bottom Housing | PN-0163-00
| Tools/Equipment: | Part#

Critical Process Parameters

Critical Quality Attributes

Ensure o-ring is securely within groove

Key Points

# Top Sub-Assembly

## Note: Bottom and top sub-assemblies are

## independent and not sequential

Seq # | Cycle Time | Operation Description | Using sensor strip assembly built previously (work instructions) (https://docs.google.com/presentation/d/1mmg70wa4t9VDHZ8DcKersijUVMYjF6ISbV-74Fe6928/edit?usp=sharing) insert cables through grommet in order of longest to shortest (Blue-Green-Red-Yellow-Purple). Be careful when pushing on back end of wires to avoid damage, use plastic pliers as necessary to pull connectors through. Wires should enter through narrow side and exit on wider, flanged side

01

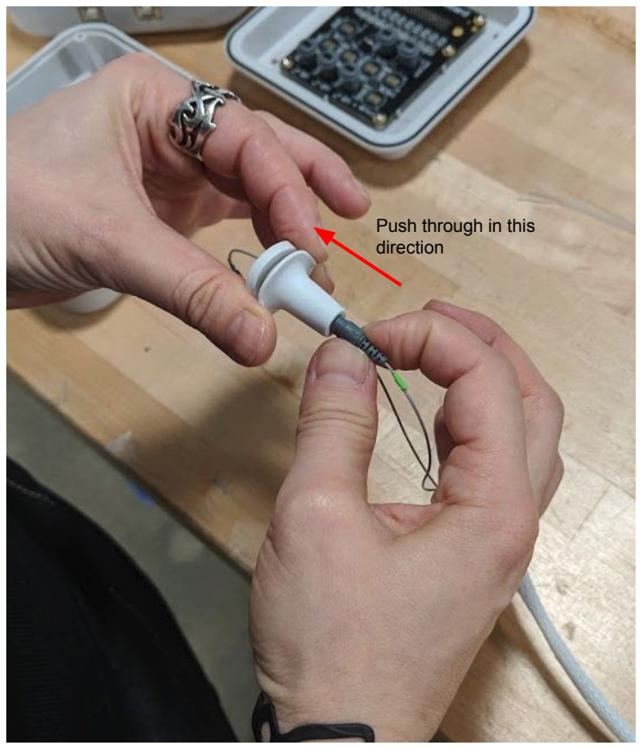
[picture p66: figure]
Push through in this direction

| Part Desc: | Part#
| Sensor Strip Assembly Grommet | BOM-0284-00 PN-0168-00
| Tools/Equipment: | Part#

Critical Process Parameters

Critical Quality Attributes

Do not apply push on back end of wires to thread through grommet

Key Points

Connectors should exit on wide, flanged side of grommet

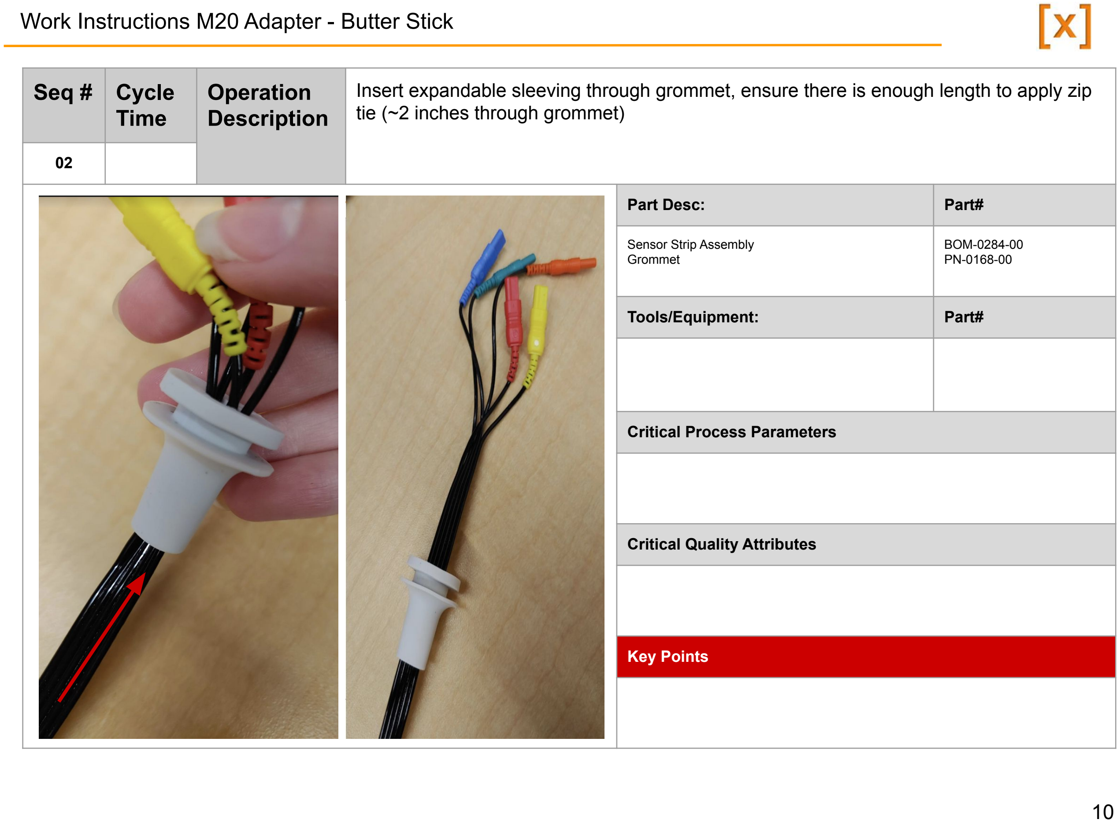
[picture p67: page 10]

Seq # | Cycle Time | Operation Description | Insert expandable sleeving through grommet, ensure there is enough length to apply zip tie (~2 inches through grommet)

02

| Part Desc: | Part#
| Sensor Strip Assembly Grommet | BOM-0284-00 PN-0168-00
| Tools/Equipment: | Part#

Critical Process Parameters

Critical Quality Attributes

Key Points

Seq # | Cycle Time | Operation Description | Pull all 5 cables through hole on top housing. It is recommended to start with the longest cable first and end with the shortest.

06

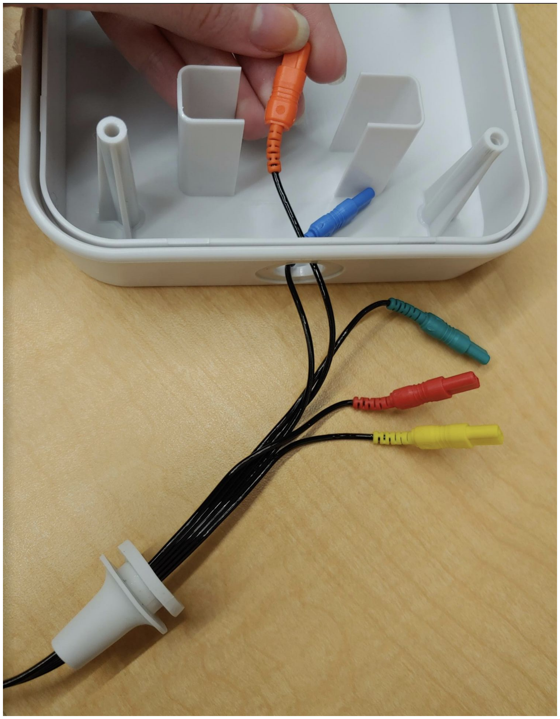
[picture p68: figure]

| Part Desc: | Part#
| Sensor Strip Assembly Top Housing
| Tools/Equipment: | Part#

Critical Process Parameters

Critical Quality Attributes

Key Points

Seq # | Cycle Time | Operation Description | Pull expandable sleeving through hole on top housing. Note: if zip ties are not tight enough they will not fit through the hole

07

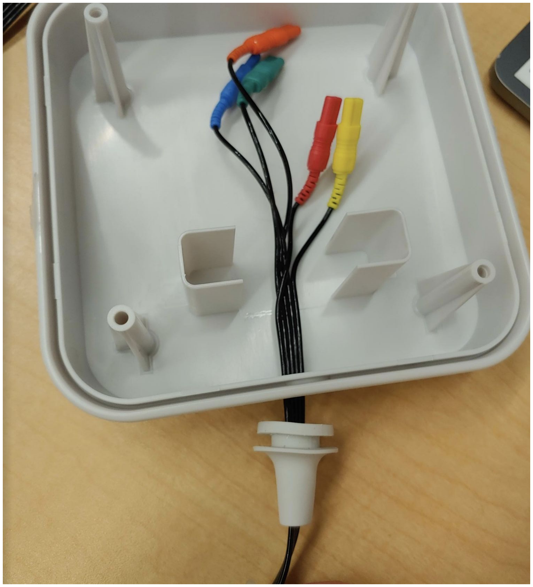
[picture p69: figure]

| Part Desc: | Part#
| Sensor Strip Assembly Top Housing
| Tools/Equipment: | Part#

Critical Process Parameters

Critical Quality Attributes

Key Points

Seq # | Cycle Time | Operation Description | Using your fingers, push the grommet flange through the hole on the top housing as shown. Gently pull back on sleeve/cables until the edge is up against the flange

08

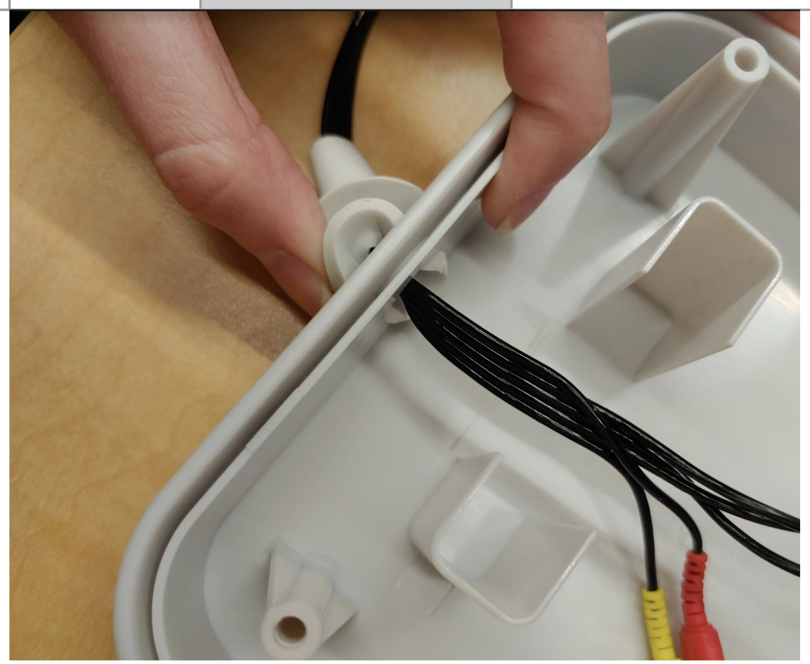
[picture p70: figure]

| Part Desc: | Part#
| Grommet Sensor Strip Assembly Top Housing
| Tools/Equipment: | Part#

Critical Process Parameters

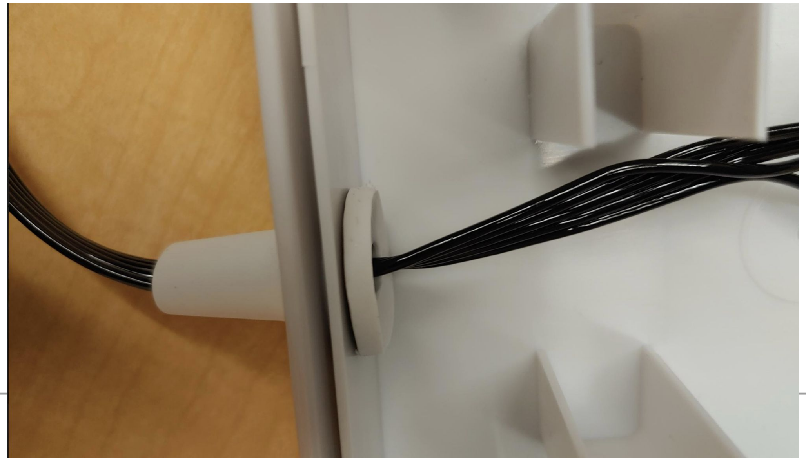
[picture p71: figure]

Critical Quality Attributes

Key Points

# Final Assembly

Seq # | Cycle Time | Operation Description | Connect sensor strip wires to Breakout Board Blue → CH 1 Green → CH 2 Orange → CH 3 Yellow → BIAS/GND Red → REF

29

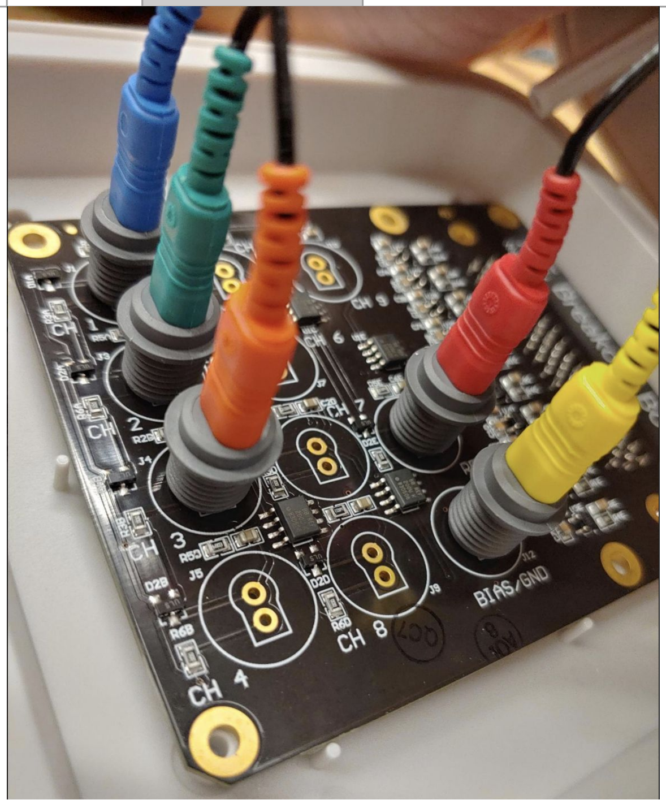
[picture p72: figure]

| Part Desc: | Part#
| Top Sub-Assembly Bottom Sub-Assembly
| Tools/Equipment: | Part#

Critical Process Parameters

Critical Quality Attributes

Key Points

Seq # | Cycle Time | Operation Description | Align top and bottom housings and close. Fasten qty 4 M3.36x10 screws to bottom housing in a star pattern. Torque to 8.5 in-lbs

30

| Part Desc: | Part#
| Bottom Housing Torx M3.36x10 (x4) | PN-0163-00 PN-0216-00

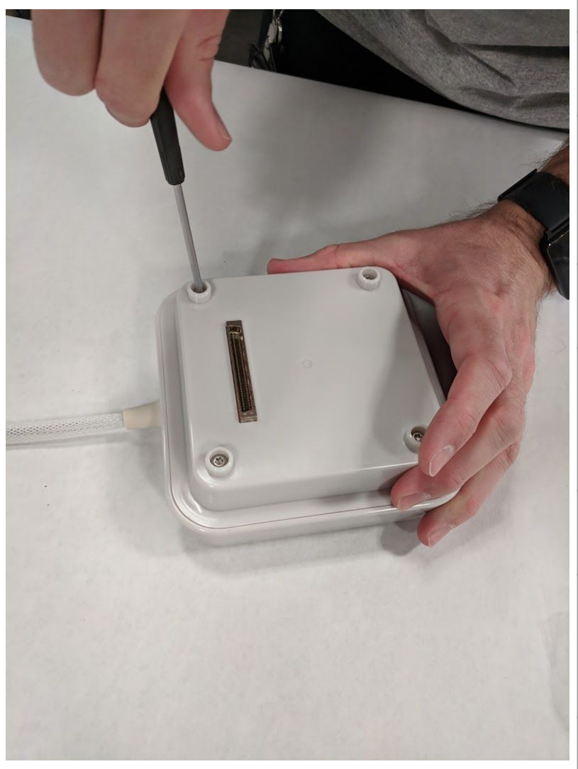
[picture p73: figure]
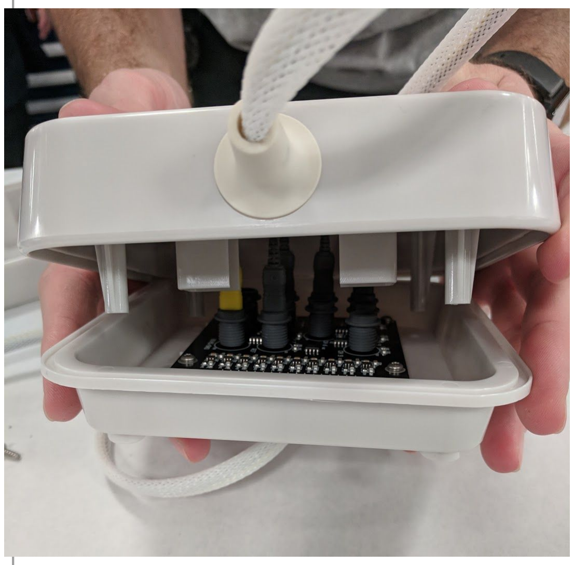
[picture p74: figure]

| Tools/Equipment: | Part#
| T15 Torque Driver

Critical Process Parameters

8.5 in-lbs tightening torque

Critical Quality Attributes

Screws should fully seat

Key Points

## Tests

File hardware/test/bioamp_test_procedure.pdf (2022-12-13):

# Bioamp Functional Test Procedure

2019-06-13

### Google

Doc #:
Revision: 01

xxx-xxxxx-xx
Rev 01

### Work Instruction

## Table of Contents

Document History

Scope

Safety Controls & Requirements

1.0 Functional Test
1.1 Test Equipment
1.2 Overview
1.3 Criteria
1.4 Test Setup and Procedure 1.5 Preventative Maintenance 1.6 Troubleshooting

Questions/Comments

Google | Confidential and Proprietary | [X]

## Document History

Rev | History/Change Description | Originator(s) | Approver | Date
01 | Initial Draft | Zoey Zweber

## Scope

This test demonstrates bioamp output per given input in the form of square waves. A signal is generated from the bioamp output test fixture, acting as an input to the bioamp which then reports output. The output is analyzed to ensure that the amplitude and frequency of the detected output fall within the tolerance of the expected values. The test will identify if any of the 32 available channels are not functional or accurate.

## Safety Controls & Requirements

- Test must be conducted in an environment that is free from external disturbances such as vibration, as this could alter the device connection and consequently test results.
- Environment must be clear of all non-essential electronic devices.

## 1.0 Functional Test

## 1.1 Test Equipment

1 | Device Under Test - Bioamp (Flashed with firmware)

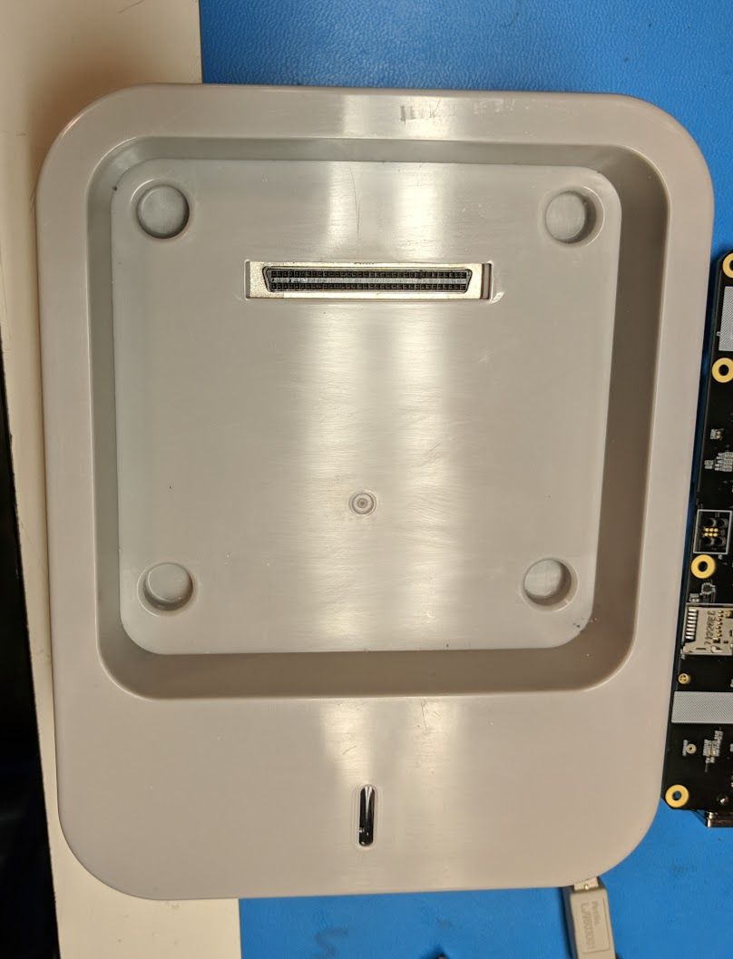
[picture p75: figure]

2 | Additional test equipment

Philo provided laptop containing : 1x USB A interface; io-test script installed, Logs folder mapped

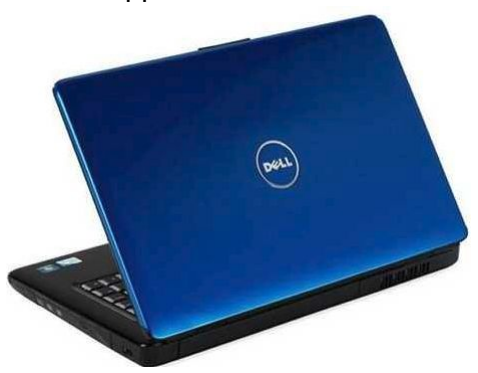
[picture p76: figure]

1x USB A/B cables

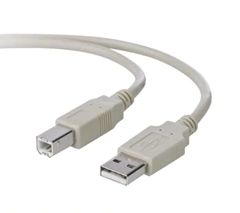
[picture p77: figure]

1x Barcode Scanner

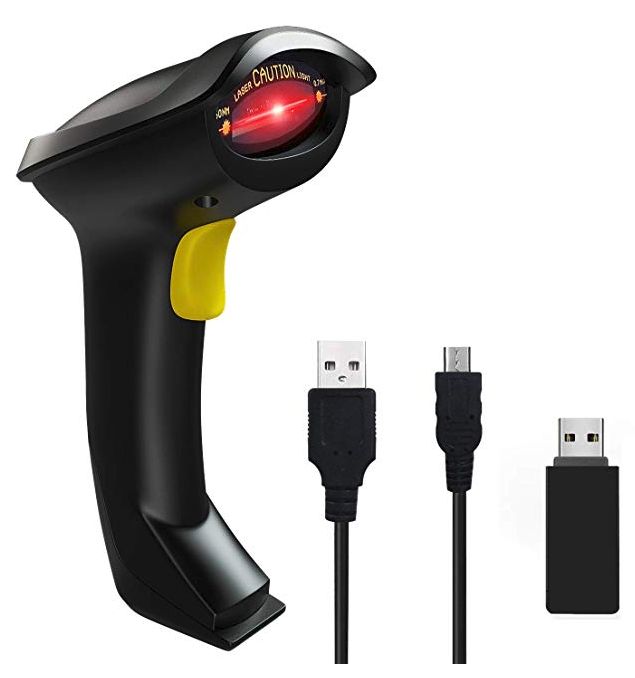
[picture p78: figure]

Bioamp Output test fixture

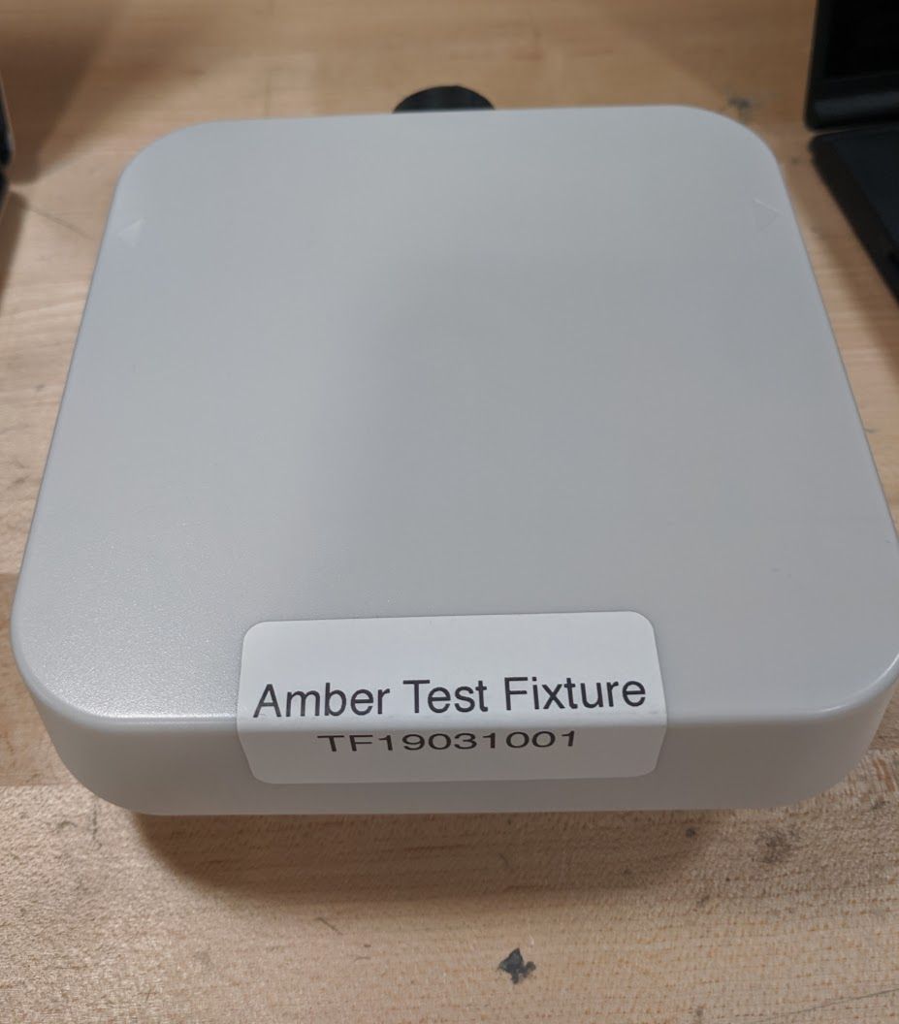
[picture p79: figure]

## 1.2 Overview

Test | Description
Bioamp Functionality Test | Measures the output signal accuracy, differential offset, and frequency response of all 32 channels per given input from test fixture

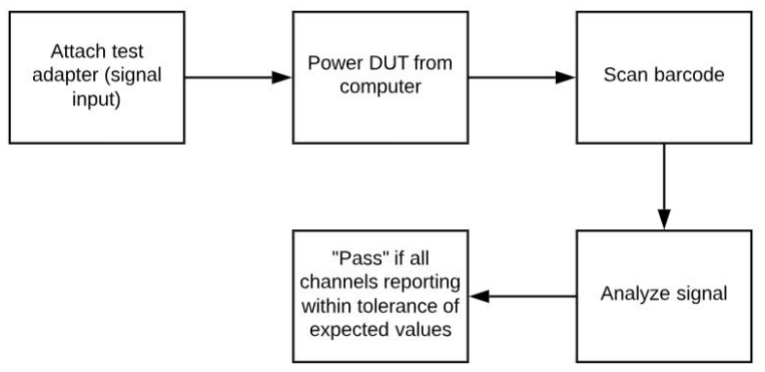
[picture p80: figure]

## 1.3 Criteria

Criteria | Description
Accuracy of signal reproduction | Input signals in the range of ±0.5 mV, varying at a rate to 12 mV/s, shall be reproduced on the output with an error of ≤ ±20 % of the nominal value of the output or ±10 μV, whichever is greater
Input dynamic range and differential offset voltage | With a d.c. offset voltage in the range of ±300 mV and differential input signal voltages of ±0.5 mV that vary at rates up to 12 mV/s, when applied to any lead wire, the time-varying output signal amplitude shall not change by more than ±10 % over the specified range of d.c. offset.
Frequency response | A frequency response (bandwidth) of at least 0.5 Hz to 50 Hz when tested with sinusoidal input signals. The output at 0.5 Hz and 50 Hz shall be within 71 % to 110 % of the output obtained with a 5 Hz sine wave input signal

## 1.4 Test Setup & Procedure

Step | Action
1 Attach test adapter. Press down firmly to ensure it is fully seated on bioamp. | Note- test adapter will have different labeling than unit pictured

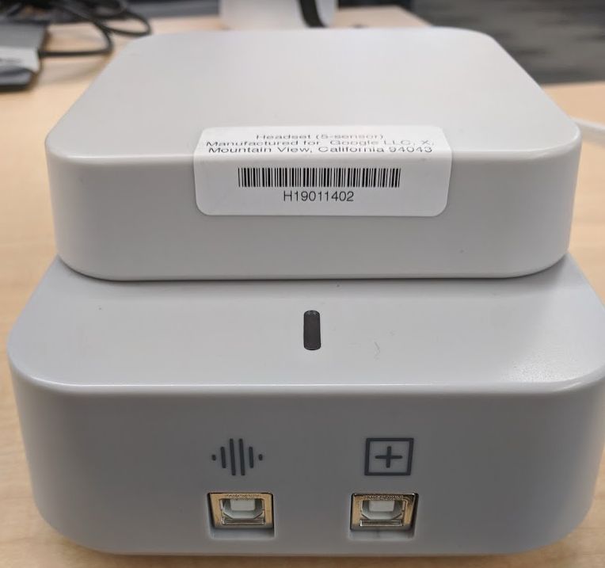
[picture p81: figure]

### 2 Connect and power Bioamp to Laptop - Connect USB cable (B side) to Data port

on Bioamp and USB (A side) to computer. This will power up the PCB (green LED illuminated)
Note- only plug in one device at a time

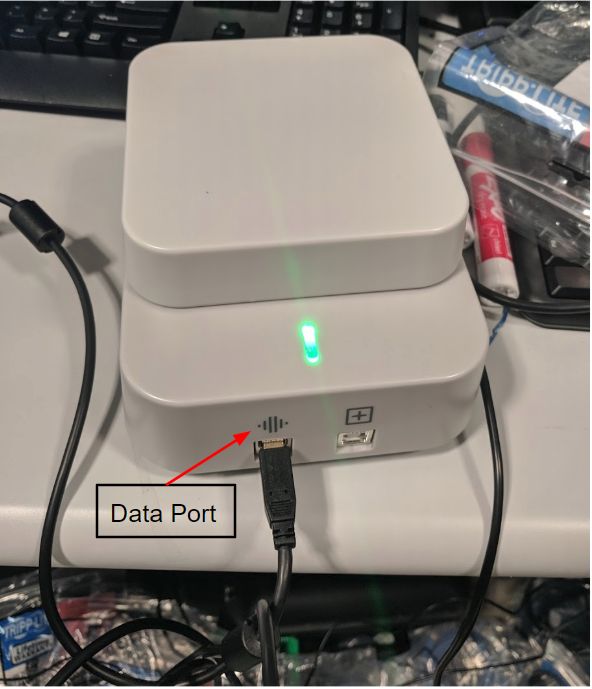
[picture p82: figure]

### 3 Double click “io-test” icon from desktop to open test script

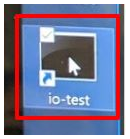
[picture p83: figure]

### 4 Enter operator name or ID as prompted

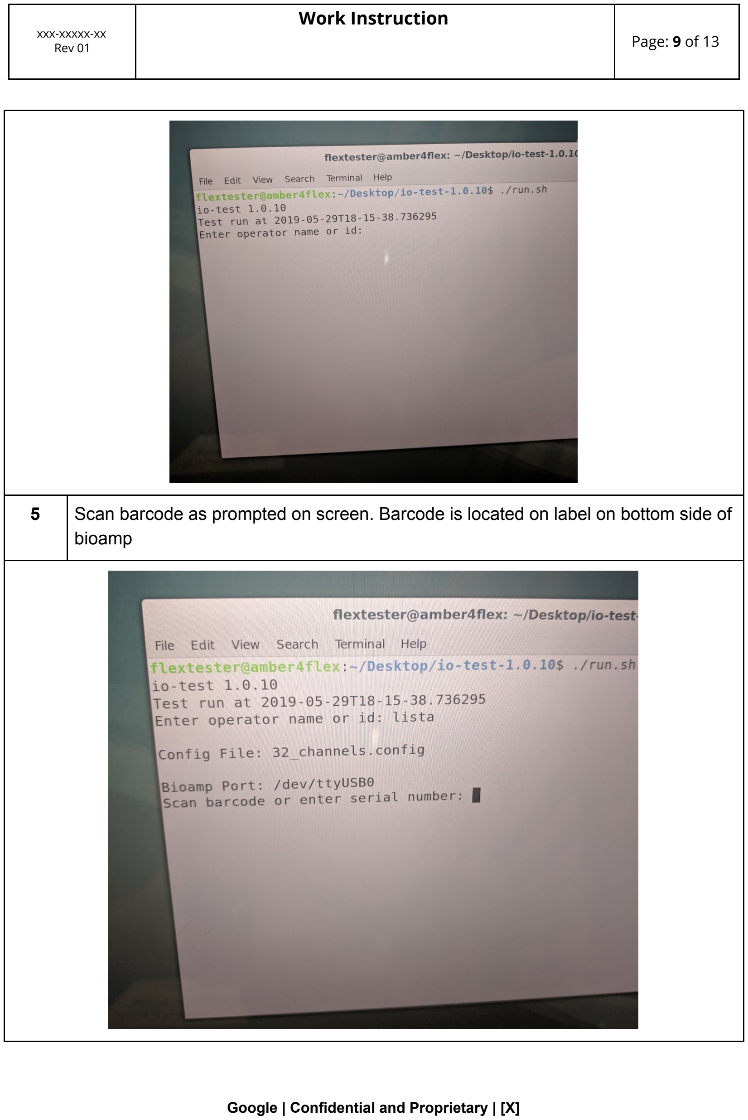
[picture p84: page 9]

### 5 Scan barcode as prompted on screen. Barcode is located on label on bottom side of

bioamp


### 6 Return bioamp to upright position on table. Press down on test adapter to ensure

solid connection to bioamp.


7 Hit “Enter” to initiate test.
Note- Do not disturb unit while test is running


### 8 Test results will populate as pass or fail for each of the 32 channels. Test logs are

also copied to “Logs” folder located on desktop


9 Close the test script window. Unplug DUT.
Note- you must close the script window or click “Relaunch” in between each device tested

## 1.5 Preventative Maintenance

Type | Action

Daily

Before Batch Testing

Bi-Monthly

## 1.6 Troubleshooting

# | Symptom | Likely Cause

1 | “Access denied” error shows when opening io-test script | Script cannot be run while Visualizer is open. Close visualizer and attempt to open test script again.
2 | Test script crashes before it finishes running | Known software bug, unplug and replug the DUT and then rerun test
3 | Very few channels show results and all fail | Adapter is likely not completely seated on the bioamp
4 | Test does not display results for all 32 channels | Issue with USB connection. Recommend unplug and replug in

## Questions/Comments

Provide contact info for any questions pertaining to this document.

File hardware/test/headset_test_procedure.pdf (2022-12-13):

# 990-03958-00 Headset Test Procedure

For GPN: 710-03085-02 ASSY, ELEC-MECH, M20 HEADSET,

### BUTTER STICK, AMBER

### Google

Doc #: 990-03958-00
Revision: 01

xxx-xxxxx-xx
Rev 01

### Work Instruction

## Table of Contents

Document History

Scope

Safety Controls & Requirements

1.0 Functional Test
1.1 Test Equipment
1.2 Overview
1.3 Test Setup and Procedure 1.4 Preventative Maintenance 1.5 Troubleshooting

Questions/Comments

Google | Confidential and Proprietary | [X]

## Document History

Rev | History/Change Description | Originator(s) | Date
-- | Initial Draft | Zoey Zweber
-- | Updated for new test fixture | Zoey Zweber | 2019/11/06
01 | Updated process | Gabriella Levine | 2019/12/16

## Scope

This test demonstrates the adapter assembly is receiving signal through each sensor and that each sensor is associated with the correct channel on the amplifier input, and assembled in its correct location on the sensor strip. Signals are generated from the test fixture at a known frequency and amplitude. These signals are received through the sensor strip and the output is analyzed to ensure that the amplitude and frequency of the detected output fall within the tolerance of the expected values (as defined in product PRD and IEC 60601-2-26 standard). The test will identify if any of the sensors are not functional or accurate. Each test is performed with a “golden” bioamp to separate performance issues between the bioamp and adapter assemblies.

## Safety Controls & Requirements

- Test must be conducted in a clean and dry environment.

## 1.0 Functional Test

## 1.1 Test Equipment

1 | Device Under Test (DUT) - Headset assembly


2 | Golden Bioamp

3 | Headset test fixture


4 | Additional test equipment

Philo provided laptop containing : 1x USB A interface; io-test script installed, Logs

folder mapped


2x USB A/B cables


1x Barcode Scanner


1x USB powerport

## 1.2 Overview

Test | Description
Sensor Test | Measures the output signal accuracy of each sensor per given input from test fixture


## 1.3 Test Setup & Procedure

Step | Action
1 Connect and power Bioamp to Laptop - Connect USB cable (B side) to Data port | on Bioamp and USB (A side) to computer. This will power up the PCB (green LED illuminated) Note- only plug in one device (golden bioamp + DUT) at a time to the computer


### 2 Connect and power test fixture to the powerport via USB cable (B side) and the USB

cable (A side) to the powerport. Plug the powerport into the wall.
Note: There is no visual indication or LED showing that the test fixture is powered on. The sensor strip should not be plugged in yet, although it is plugged in in this photo.


3 Attach sensor strip to test fixture by securely snapping 3 sensors onto test fixture, starting with the top snap and moving downward, then connect bias and ground. 3 sensor strip → bottom snap will be unpopulated

### 4 Attach adapter assembly (DUT) to golden bioamp. Press down firmly to ensure it is

fully seated on bioamp.
Note- adapter will have different labeling than unit pictured


### 5 Double click “io-test” icon from desktop to open test script


6 Enter operator name or ID as prompted

7 Scan barcode as prompted on screen | Note: barcode for production units will be on the top surface of the adapter


### 8 WAIT 10 seconds before proceeding…

Hit “Enter” to initiate test.
Note- Do not disturb unit while test is running

### 9 Test results will populate as pass or fail for each of the sensors. Test logs are also

copied to “Logs” folder located on desktop

If the results indicate “fail”, unplug and replug the amp. Close out of the test terminal window and relaunch the “io test”, run the test again, up to a total of 3 times per DUT.


10 Remove headset snaps from fixture, and adapter from golden bioamp.

### 11 Press ‘n’ to promt the test for the next headset. (Note - if you need to unplug the

bioamp and replug it in for any reason, press ‘e’ to close and reopen the serial port, or close the terminal window and re-click on the icon to re-begin the test).

## 1.4 Preventative Maintenance

Type | Action

Daily

Before Batch Testing

Bi-Monthly

## 1.5 Troubleshooting

# | Symptom | Likely Cause

1 | “Access denied” error shows when opening io-test script | Script cannot be run while Visualizer is open. Close visualizer and attempt to open test script again.
2 | Test script crashes before it finishes running | Known software bug, unplug and replug the DUT and then rerun test

3 | Very few channels show results and all fail | Adapter is likely not completely seated on the bioamp
4 | Test does not display results for all channels | Issue with USB connection. Recommend unplug and replug in

## Questions/Comments

Provide contact info for any questions pertaining to this document.

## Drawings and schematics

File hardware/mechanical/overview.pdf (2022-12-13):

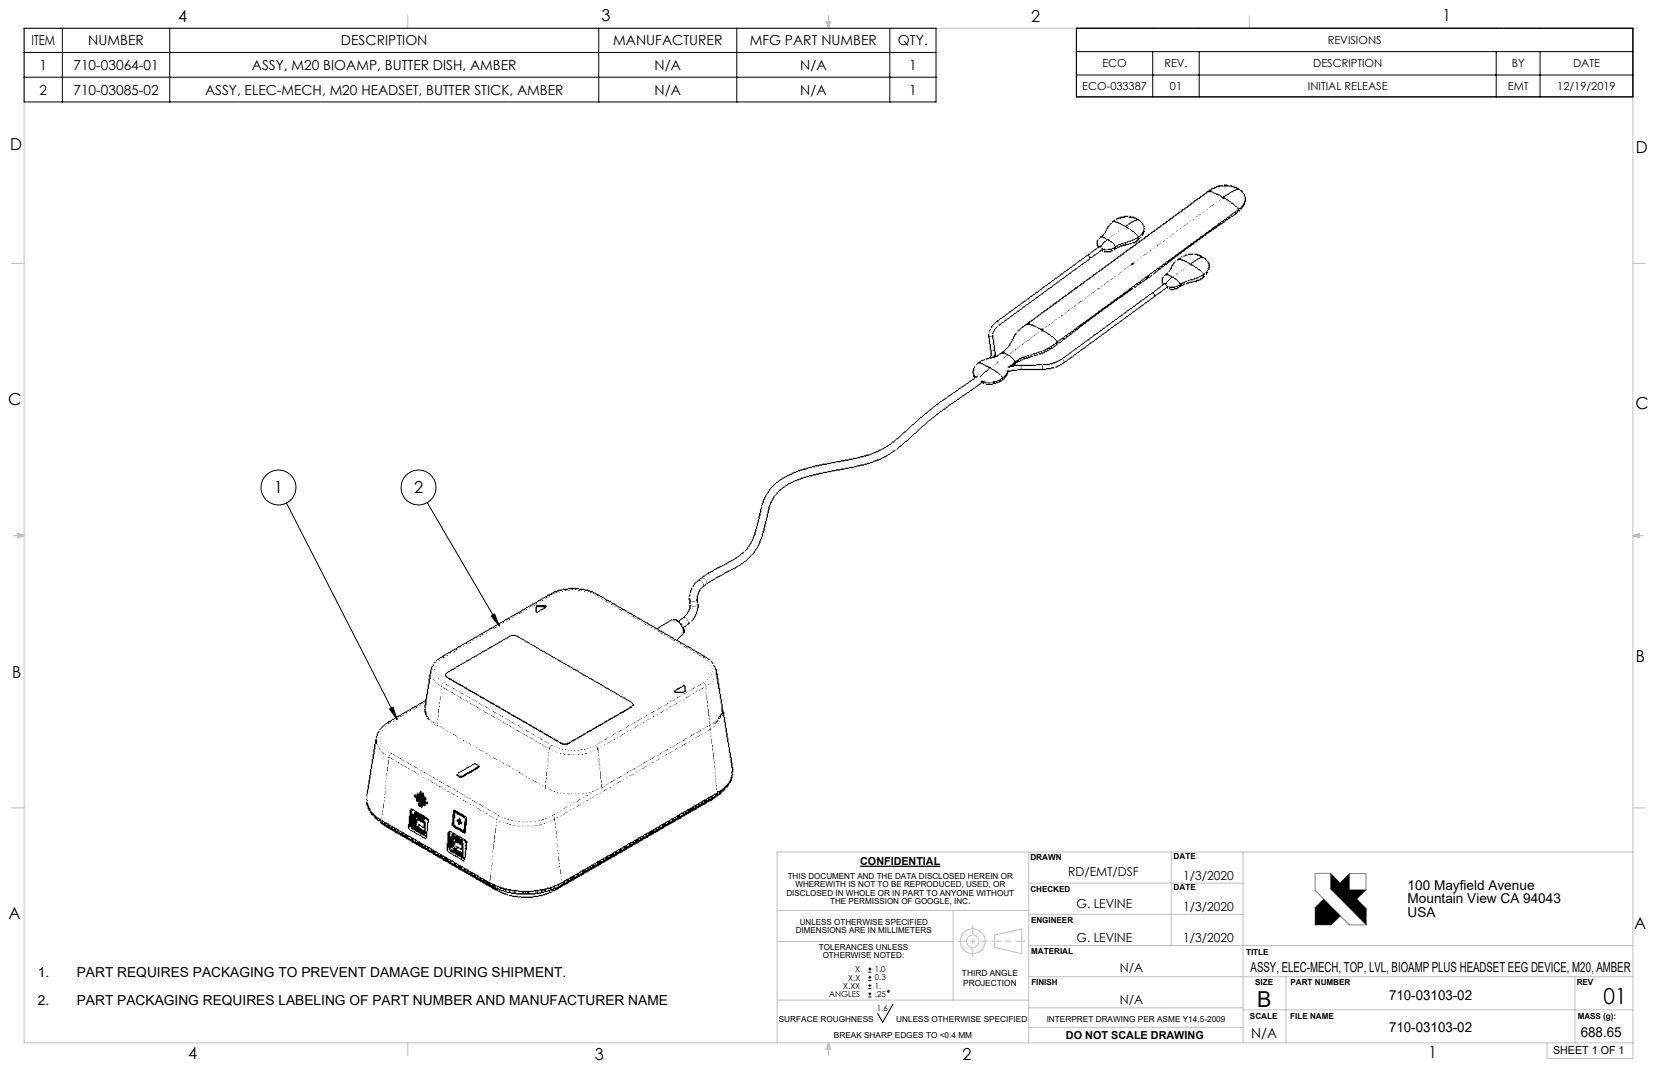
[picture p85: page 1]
ECO-033387; INITIAL RELEASE; EMT; ITEM; NUMBER; DESCRIPTION; MANUFACTURER; MFG PART NUMBER; QTY.; ASSY, M20 BIOAMP, BUTTER DISH, AMBER; ASSY, ELEC-MECH, M20 HEADSET, BUTTER STICK, AMBER; SHEET 1 OF 1; 01 REV; G. LEVINE; THIRD ANGLE; PART NUMBER; MASS (g):; FILE NAME; UNLESS OTHERWISE SPECIFIED DIMENSIONS ARE IN MILLIMETERS; TOLERANCES UNLESS OTHERWISE NOTED:; SURFACE ROUGHNESS; UNLESS OTHERWISE SPECIFIED

THIS DOCUMENT AND THE DATA DISCLOSED HEREIN OR
WHEREWITH IS NOT TO BE REPRODUCED, USED, OR
DISCLOSED IN WHOLE OR IN PART TO ANYONE WITHOUT

100 Mayfield Avenue
Mountain View CA 94043
USA

THE PERMISSION OF GOOGLE, INC.

TITLE
ASSY, ELEC-MECH, TOP, LVL, BIOAMP PLUS HEADSET EEG DEVICE, M20, AMBER
SIZE

1. PART REQUIRES PACKAGING TO PREVENT DAMAGE DURING SHIPMENT.
2. PART PACKAGING REQUIRES LABELING OF PART NUMBER AND MANUFACTURER NAME

INTERPRET DRAWING PER ASME Y14.5-2009
710-03103-02 DO NOT SCALE DRAWING

BREAK SHARP EDGES TO <0.4 MM

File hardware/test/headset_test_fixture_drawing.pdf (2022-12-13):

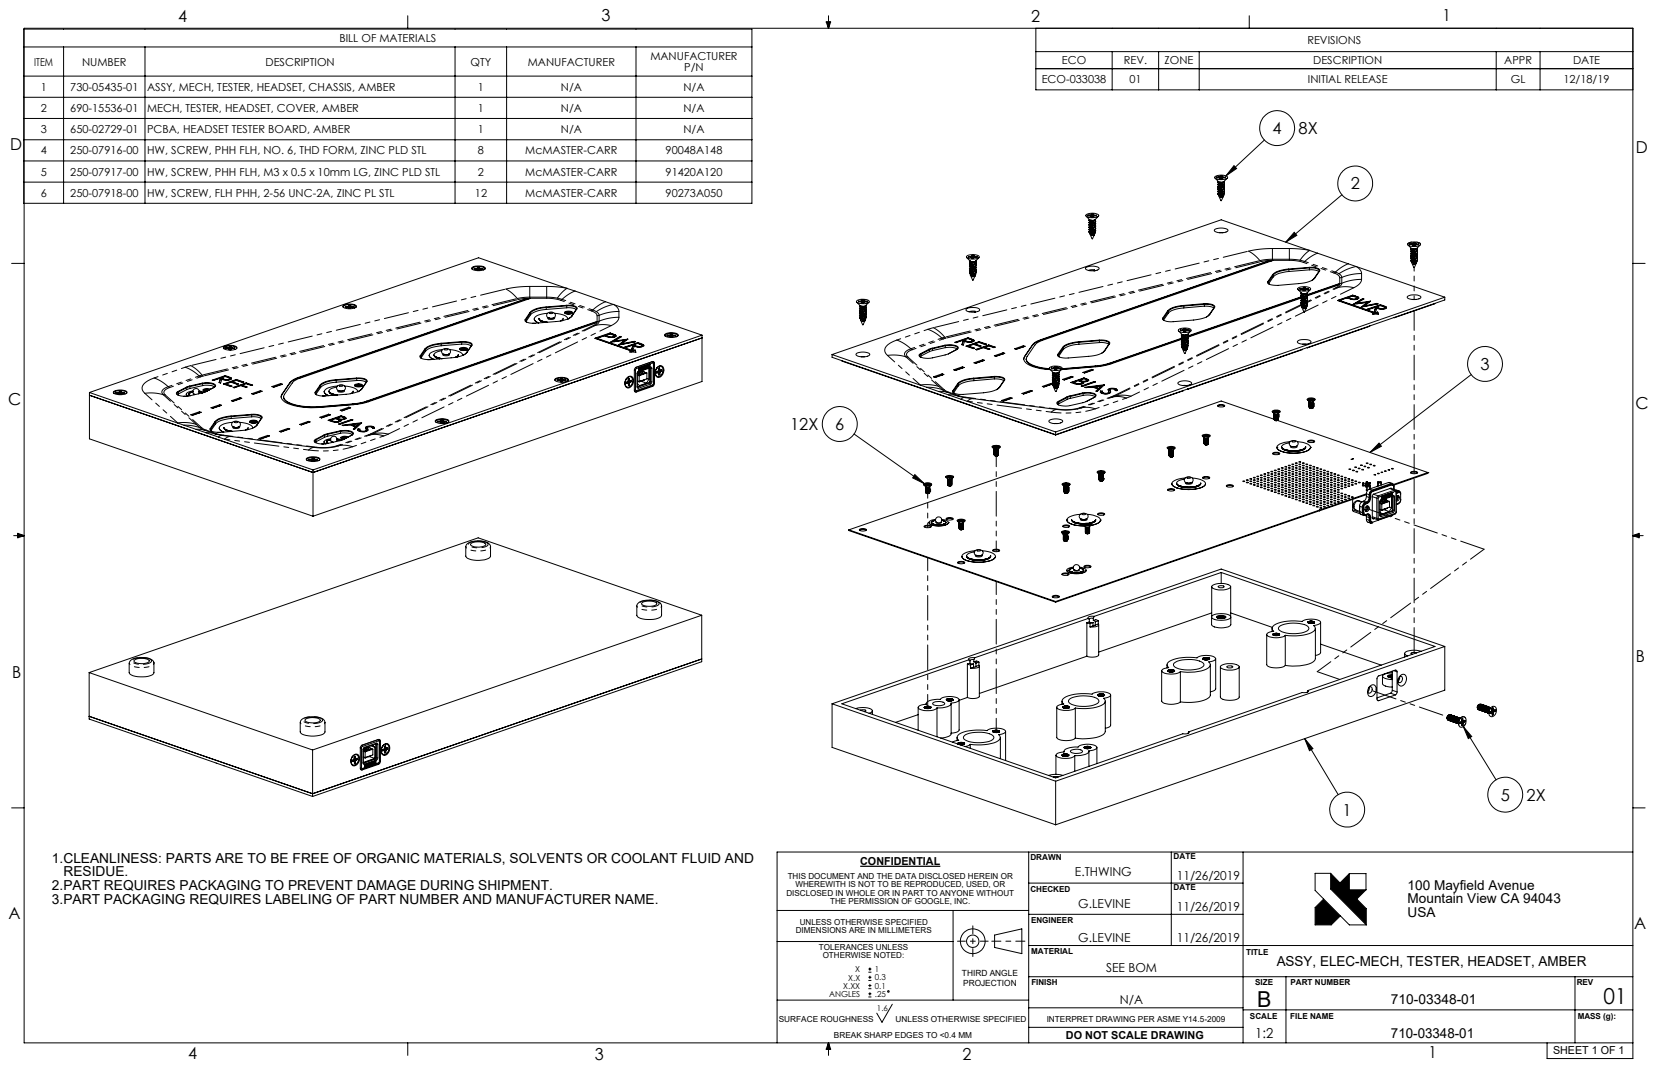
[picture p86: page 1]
SHEET 1 OF 1; 01 REV; DO NOT SCALE DRAWING; THIRD ANGLE; PART NUMBER; MASS (g):; FILE NAME; SURFACE ROUGHNESS; SEE BOM

BILL OF MATERIALS

ITEM | NUMBER | DESCRIPTION | QTY | MANUFACTURER | MANUFACTURER P/N

ECO | REV. | ZONE | DESCRIPTION | APPR | DATE
ECO-033038 | 01 | | INITIAL RELEASE | GL | 12/18/19

1 | 730-05435-01 | ASSY, MECH, TESTER, HEADSET, CHASSIS, AMBER | 1 | N/A | N/A
2 | 690-15536-01 | MECH, TESTER, HEADSET, COVER, AMBER | 1 | N/A | N/A
3 | 650-02729-01 | PCBA, HEADSET TESTER BOARD, AMBER | 1 | N/A | N/A
4 | 250-07916-00 | HW, SCREW, PHH FLH, NO. 6, THD FORM, ZINC PLD STL | 8 | McMASTER-CARR | 90048A148
5 | 250-07917-00 | HW, SCREW, PHH FLH, M3 x 0.5 x 10mm LG, ZINC PLD STL | 2 | McMASTER-CARR | 91420A120
6 | 250-07918-00 | HW, SCREW, FLH PHH, 2-56 UNC-2A, ZINC PL STL | 12 | McMASTER-CARR | 90273A050

1.CLEANLINESS: PARTS ARE TO BE FREE OF ORGANIC MATERIALS, SOLVENTS OR COOLANT FLUID AND
RESIDUE.
2.PART REQUIRES PACKAGING TO PREVENT DAMAGE DURING SHIPMENT.
3.PART PACKAGING REQUIRES LABELING OF PART NUMBER AND MANUFACTURER NAME.

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

100 Mayfield Avenue
Mountain View CA 94043
USA

THE PERMISSION OF GOOGLE, INC.

UNLESS OTHERWISE SPECIFIED
DIMENSIONS ARE IN MILLIMETERS
TOLERANCES UNLESS
OTHERWISE NOTED:
ASSY, ELEC-MECH, TESTER, HEADSET, AMBER X

INTERPRET DRAWING PER ASME Y14.5-2009

BREAK SHARP EDGES TO <0.4 MM
